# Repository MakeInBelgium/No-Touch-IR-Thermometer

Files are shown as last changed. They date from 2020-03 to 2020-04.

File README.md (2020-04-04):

# No-Touch-IR-Thermometer

## Introduction
Especially in the second phase and during the recovery of this pandemic, we will need to monitor both oursleves and our peers at work or in public places. One of the methods being used is checking whether someone has a fever or not. In order to do this without risking even more contamination, we can use *NO-TOUCH Thermometers*. Like the ones you use to test a baby's temperature.

We already anticipate a lack of enough available devices and are looking for **affordable** and **scalable** solutions. 

## GOALs
1) Using the occam's razor method we want to strip the concept of all unnecessary parts. The *need* we want to solve here is not knowing how high someone's temperature is. We merely want to know whether or not someone is a risk. Basic **triage**. Therefor we could eliminate an LED screen for example from the list of components and use just a GREEN/ORANGE/RED status indicator. 
2) We also want this to be something that van be (re)created wherever in the world with as little as possible equipment and components. This to drive down the cost, limit the skillset needed to finish the project, and limit the materials that need to be sourced.

## Concepts
There are 2 design concepts we have come up with. Both are based on the exact same principles but have a slightly different approach in building. Both are using an 8-bit Microcontroller that can be flashed through an Arduino set-up, and a [Melexis FIR](https://www.melexis.com/en/product/MLX90614/Digital-Plug-Play-Infrared-Thermometer-TO-Can) (Far Infra Red Temperature Sensor). Furthermore there's just a push button, a green/orange/red LED light and some electrical components. That's it!

### Project *Tiny-FIR*
The Tiny-FIR is based on the [ATtiny85](https://www.microchip.com/wwwproducts/en/ATtiny85) and will be a fully assembled PCB board. The designs for the board and all necessary information to recreate van be fond in the Tiny_FIR folder. 
*Audience*: this model is targeted at makerspaces and manufacturers

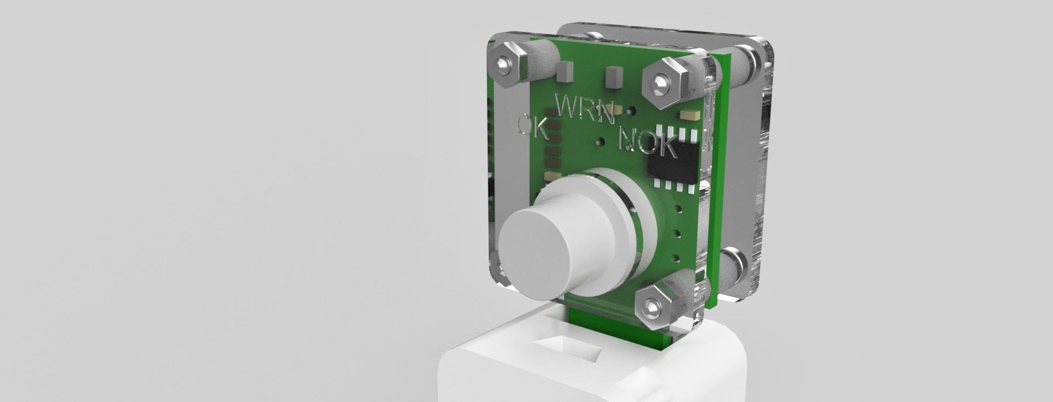
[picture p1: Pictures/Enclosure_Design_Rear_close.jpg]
Rear Close

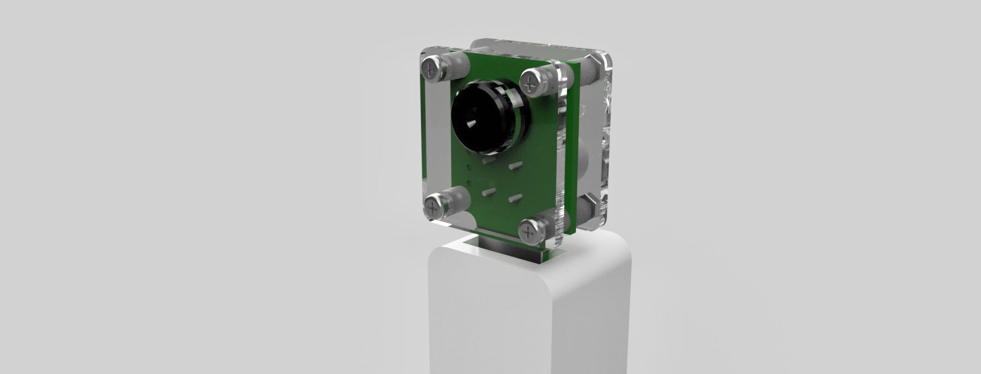
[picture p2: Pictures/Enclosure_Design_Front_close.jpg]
Rear Close


### Project *Mega-FIR*
the Mage-FIR is based on the [ATmega328](https://www.microchip.com/wwwproducts/en/ATmega328) and will be a default prototype breadboard with pin-though-hole components. The idea here is that all components are readily available off the shelf without the need for 3rd party manufacturers.
*Audience*: literally everyone with an Arduino board and a soldering iron.

doesn't she look cute?

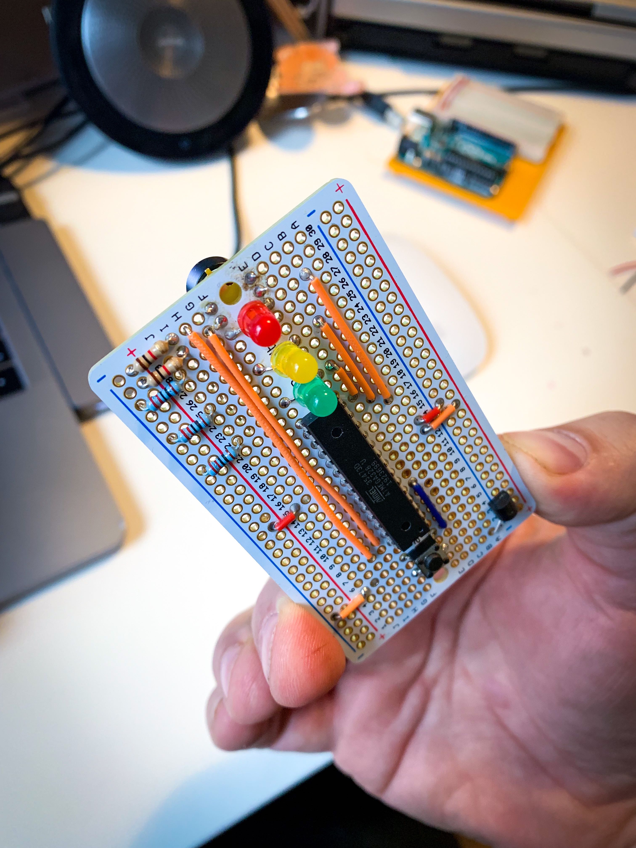
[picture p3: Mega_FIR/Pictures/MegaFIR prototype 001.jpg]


## Supported by:
* [EuroCircuits](https://www.eurocircuits.com/) - is helping with the first batches of the PCB-boards
* [MELEXIS](https://www.melexis.com/en) - has provided a first set sensors for the prototypes

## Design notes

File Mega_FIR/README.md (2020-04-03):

# The MegaFIR
 
## Introduction
The MegaFIR was the original concept of this no-touch-thermometer project. The ideas was for everyone with a soldering iron and a credit card to be able to build a fever triage thermometer. This is how it currently looks like in pretotyping. Feel free to check the [Electrical Diagram](https://github.com/MakeInBelgium/No-Touch-IR-Thermometer/blob/master/Mega_FIR/MegaFIR_ElectricalDiagram.md) document and the [Build of Materials (BoM)](https://github.com/MakeInBelgium/No-Touch-IR-Thermometer/blob/master/Mega_FIR/MegaFIR_BoM.md). 



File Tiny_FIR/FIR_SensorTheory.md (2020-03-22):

# Theory of operation
## Non-contact thermometers
**Disclaimer:** normal body temperature is considered to be 37°C; however, a wide variation is seen.<sup>[1](#cit1)</sup> So a measument taken  from a DIY device and judged to be either norminal or fibrile by that DIY device should *never be used in critical situations!*. The configuration of this concept is for TRIAGE puproses only.

There are several methods to measure body temperature. In the category of radiometric (infrared) measurements there are 3 main methods<sup>[2](#cit2)</sup>:
1. Tympanic thermometer (eardrum temperature)
2. Handheld skin thermometers (infrared sensors)
3. Thermal scanners (infrared cameras)

The Tiny_FIR project aims to build a sensor that uses this second measuring method, measuring the surface temperature of the skin. Because the sensor used in the Tiny_FIR and Mega_FIR project is also widely used for Tympanic thermometers, care must be taken to use and reference the right information online. The fibrile temperature is different for the eardrum than the skin surface and most probably a different compensation approuch should be used to determine the body temperature.

Most of the clinical radiometric thermometers that use the tympanic or skin surface measurements will report the body temperature. This temperature is a calculated, or indirect, measurement. Most of the Thermal cameras are general purpose devices that only report the direct measurent not the indirect body temperature.

The ideal fibrile threshold temperature of the skin surface seems to range between 37.5°C and 38°C. <sup>[3](#cit3)</sup>

## FIR sensors
The MLX90614 comes in many flavors. Melexis proposes to use the MLX90614-DCC. 
- D: This means the device is calibrated for 0.2degC accuracy around body temperature.
- C: The device is compensating for (but not eliminating) thermal gradients. 
- C: There is a 35 degree FOV.

In order to achieve as much accuracy as possible, there are some good practices to be followed:
### Ambient temperature
The temperature readout from the sensor (To) is compensated internally by the ambient temperature (Ta) as such: V<sub>ir</sub> = A x (To<sup>4</sup>-Ta<sup>4</sup>) The measurment of Ta is taken internally by a PTAT sensor. To achieve a higher accuracy this PTAT sensor measures the ambient temperature. In other words: the sensor should be in total thermal equilibrium with the surroundings.

The electronic design of the Tiny-FIR is in such a way so there is no large power-dissipation near the sensor. Furthermore, the sensor is kept powered all the time in between measurements as long as it is used (plugged into the USB powerbank). This avoid thermal gradients due to self-heating.

Lastly the user should be informed that usage of this sensor is limited to thermally static conditions. This means, for example, that **the sensor cannot be used in outdoor high-wind conditions** or when switching between area's with different ambient temperatures, like indoor and outdoor.

As a side-note it should be noted that a more complex compensation algorithm to calculated the body temperature should also use the ambiant temperature. The thermal gradient from body to skin surface will be depend on the ambiant temperature. So we can conclude that the fibrile temperature of the skin surface will also be ambient temperature dependent. This is also the reason why Ta is available for readout on the MLX90614.

### Field of view
The FOV of the sensor is defined as the region where it has more that 50% sensitivity. It is important that the surface that needs to be measured in entirely in the FOV. Some commercial thermometers achieve this by having two cocussed light beams converge, so when the dot allign the sensor is at the right distance.

Further investigation here is still required on how to implement this.

-----
# References:
1. : https://www.ncbi.nlm.nih.gov/books/NBK331/
2. : https://www.ncbi.nlm.nih.gov/books/NBK263242
3. : https://www.eurosurveillance.org/images/dynamic/EE/V14N06/art19115.pdf

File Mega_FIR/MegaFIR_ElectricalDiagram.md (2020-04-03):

# MegaFIR Electrical Diagram

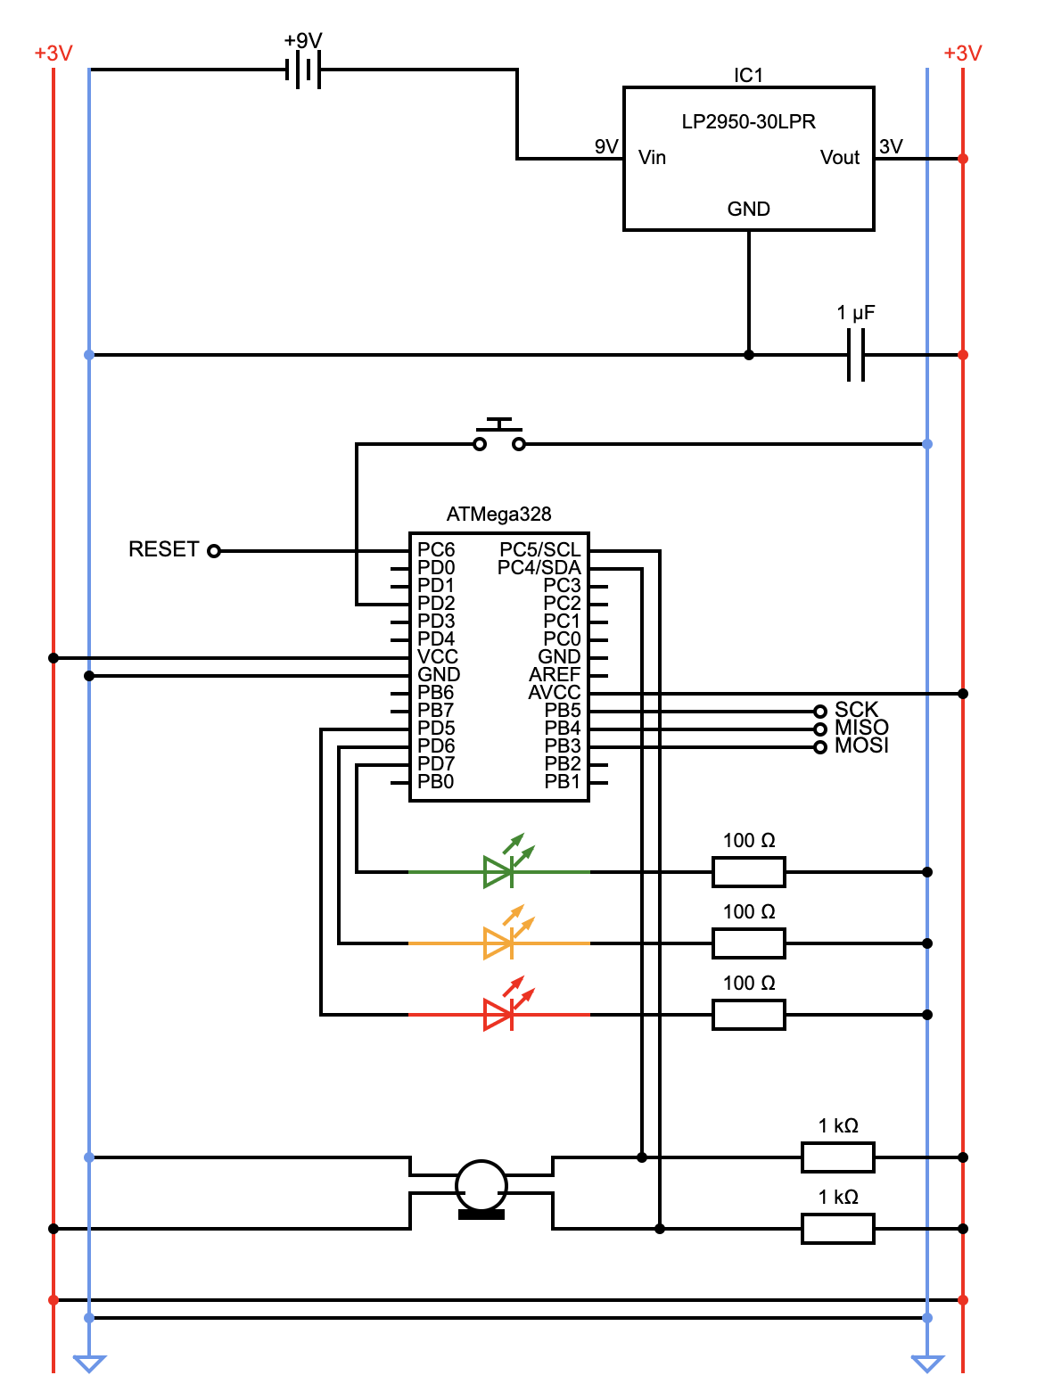
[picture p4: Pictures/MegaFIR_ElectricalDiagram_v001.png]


Note: the design is draw using Circuit Diagram, a free and Open-Source tool. [You can find the design here](https://www.circuit-diagram.org/circuits/e216c06a74a149ee9efb37499b95ee45).

## Description
This design is based on the idea of using a pin-through-hole proto-breadboard [(example)](https://www.adafruit.com/product/571) with 2x30 lanes and a +/- rail on each side. The lay-out is specifically designed to have the least amount of cables overlapping or even crossing the middle section. 

## PIN assignment
Some PINs on the ATmega are randomly chosen, some are very strict:
| ATmega PIN | Arduino PIN | Description | Strict? |
| --------: | --------: | -------- | :--------: | 
| 1 / PC6 | RESET | needed for programming the ATmega from the Arduino | X |
| 4 / PD2 | 2 | input from switch/button |  |
| VCC | VCC | Power | X |
| GND | GND | Ground | X |
| 11 / PD5 | 5 | Output LED red | |
| 12 / PD6 | 6 | Output LED green | | 
| 13 / PD7 | 7 | Output LED orange | | 
| 28 / PC5 | A5 | SCL (clock) port 1 on the MLX | X |
| 27 / PC4 | A4 | SDA (data) port 2 on the MLX | X |
| 20 / AVCC | AVCC | Power | X |
| 19 / PB5 | 13 | SCK - needed for programming the ATmega from the Arduino | X |
| 18 / PB4 | 12 | MISO - needed for programming the ATmega from the Arduino | X |
| 17 / PB3 | 11 | MOSI - needed for programming the ATmega from the Arduino | X |

## Arduino & ATmega pin alignment

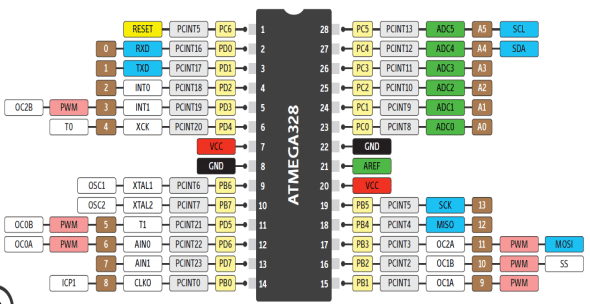
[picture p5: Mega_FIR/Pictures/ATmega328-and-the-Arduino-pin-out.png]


*sorry I can't find and quote the original source of this image. it was the best Google search result

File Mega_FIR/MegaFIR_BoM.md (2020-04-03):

# MegaFIR Build of Materials:

| # | Description | Manufacturer-ID | Farnel Code | Other Links | €/piece |
|----------|----------|----------|----------|---------|---------:|
| 1 | Melexis Sensor MLX90614 | MLX90614ESF-DCC-000 | / | [Mouser link](https://eu.mouser.com/ProductDetail/Melexis/MLX90614ESF-DCC-000-TU?qs=%2Fha2pyFaduia27wdAojmz0Gw0WK2y0hzp6DRConqg3jzJRxxBtPVbyFno%252B8k7uZuTdJKb%252Bns4tW7oym5d884Wg%3D%3D) | / |
| 1 | ATmega328 Microprocessor | ATMEGA328-PU | 1972087 [link(.be)](https://be.farnell.com/microchip/atmega328-pu/mcu-8bit-atmega-20mhz-dip-28/dp/1972087) | | €1.7000 |
| 1 | LDO Voltage Regulator (3V) | LP2950-30LPR | 3122121 [link(.be)](https://be.farnell.com/texas-instruments/lp2950-30lpr/ic-ldo-volt-reg-3v-0-1a-to-92/dp/3122121) | | €0,368 |
| 1 | 1µF electrolytic capacitor |	MCF 0.25W 100R | 9339043 [link(.be)](https://be.farnell.com/rubycon/50ml1mefc4x5/cap-1-f-50v-20/dp/8126933) | | €0.0245 |
| 1 | Tactile Switch | B3F1060 | 1960944 [link(.be)](https://be.farnell.com/omron/b3f1060/switch-flat-6x6x7-100gf/dp/1960944) | | €0.2580 |
| 1 | LED - Green T-1 3/4 (5mm), 20 mA, 2 V | L-57GGD | 2217954 [link(.be](https://be.farnell.com/kingbright/l-57ggd/led-bi-polar-5mm-green/dp/2217954) | | €0.3180 |
| 1 | LED - Yellow T-1 3/4 (5mm), 20 mA, 2 V |	L-57YYD | 2217955 [link(.be)](https://be.farnell.com/kingbright/l-57yyd/led-bi-polar-5mm-yellow/dp/2217955) | | €0.1530 |
| 1 | LED - Red T-1 3/4 (5mm), 20 mA, 2 V | L-57IID | 2217953 [link(.be)](https://be.farnell.com/kingbright/l-57iid/led-bi-polar-5mm-red/dp/2217953) | | €0.3130
| 2 | Resistor 1kΩ | MCF 0.25W 1K | 9339051 [link(.be)](https://be.farnell.com/multicomp/mcf-0-25w-1k/res-1k-5-250mw-axial-carbon-film/dp/9339051) | | €0.0245  |
| 3 | Resistor 100Ω | 	MCF 0.25W 100R | 9339043 [link(.be)](https://be.farnell.com/multicomp/mcf-0-25w-100r/res-100r-5-250mw-axial-carbon/dp/9339043)  | | €0,0245 |
| 1 | 9V Battery Snap Connector | Keystone 2238 | 1650675 [link(.be)](https://be.farnell.com/keystone/2238/battery-strap-pp3/dp/1650675) | | €1.6900 |

## Cost
The total build of materials for a MegaFIR will set you back €6 for the components. Additional costs are:
* The Melexis sensor
* a 9V battery
* a breadboard
* some wiring
* a case* 

*:we'll come up with some ideas later, maybe even a 3D printing file

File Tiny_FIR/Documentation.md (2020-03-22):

# Theory of operation
## Non-contact thermometers
First a small disclaimer. Normal body temperature is considered to be 37°C; however, a wide variation is seen.<sup>[1](#cit1)</sup> So a measument taken  from a DIY device ánd judged to be either norminal or fibrile by that DIY device should *never be used in critical situations!*

There are several methods to measure this body temperature. In the category of radiometric (infrared) measurements there are 3 main methods<sup>[2](#cit2)</sup>:
1. Tympanic thermometer (eardrum temperature)
2. Handheld infrared skin thermometers
3. Thermal scanners (infrared cameras)

The Tiny_FIR project aims to build a sensor that uses this second measuring method, measuring the surface temperature of the skin. Because the sensor used in the Tiny_FIR project is also widely used for Tympanic thermometers, care must be taken to use and reference the right information online. The fibrile temperature is different for the eardrum than the skin surface and most probably a different compensation approuch should be used to determine the body temperature.

Most of the clinical radiometric thermometers that use the tympanic or skin surface measurements will report the body temperature. This temperature is a calculated, or indirect, measurement. Most of the Thermal cameras are general purpose devices that only report the direct measurent not the indirect body temperature.

The ideal fibrile threshold temperature of the skin surface seems to range between 37.5°C and 38°C. <sup>[3](#cit3)</sup>

## FIR sensors
The MLX90614 comes in many flavors. Melexis proposes to use the MLX90614-DCC. 
- D: This means the device is calibrated for 0.2degC accuracy around body temperature.
- C: The device is compensating for (but not eliminating) thermal gradients. 
- C: There is a 35 degree FOV.

In order to achieve as much accuracy as possible, there are many good practices to be followe:
### Ambient temperature
The temperature readout from the sensor (To) is compensated internally by the ambient temperature (Ta) as such: V<sub>ir</sub> = A x (To<sup>4</sup>-Ta<sup>4</sup>) The measurment of Ta is taken internally by a PTAT sensor. So to achieve high accuracy this PTAT sensor should measure the actual ambiant temperature. In other words: the sensor should be in total thermal equilibrium with the surroundings.

The electronic design of the Tiny-FIR is in such a way so there is no large power-dissipation near the sensor. Furthermore, the sensor is kept powered all the time in between measurements as long as it is used (plugged into the USB powerbank). This avoid thermal gradients due to self-heating.

Lastly the user should be informed that usage of this sensor is limited to thermally static conditions. This means, for example, that the sensor cannot be used in outdoor high-wind conditions or when switching between area's with different ambient temperatures, like indoor and outdoor.

As a side-note it should be noted that a more complex compensation algorithm to calculated the body temperature should also use the ambiant temperature. The thermal gradient from body to skin surface will be depend on the ambiant temperature. So we can conclude that the fibrile temperature of the skin surface will also be ambient temperature dependent. This is also the reason why Ta is available for readout on the MLX90614.

### Field of view
The FOV of the sensor is defined as the region where it has more that 50% sensitivity. It is important that the surface that needs to be measured in entirely in the FOV. Some commercial thermometers achieve this by having two cocussed light beams converge, so when the dot allign the sensor is at the right distance.

Further investigation here is still required on how to implement this.

# References:
1. : https://www.ncbi.nlm.nih.gov/books/NBK331/
2. : https://www.ncbi.nlm.nih.gov/books/NBK263242
3. : https://www.eurosurveillance.org/images/dynamic/EE/V14N06/art19115.pdf

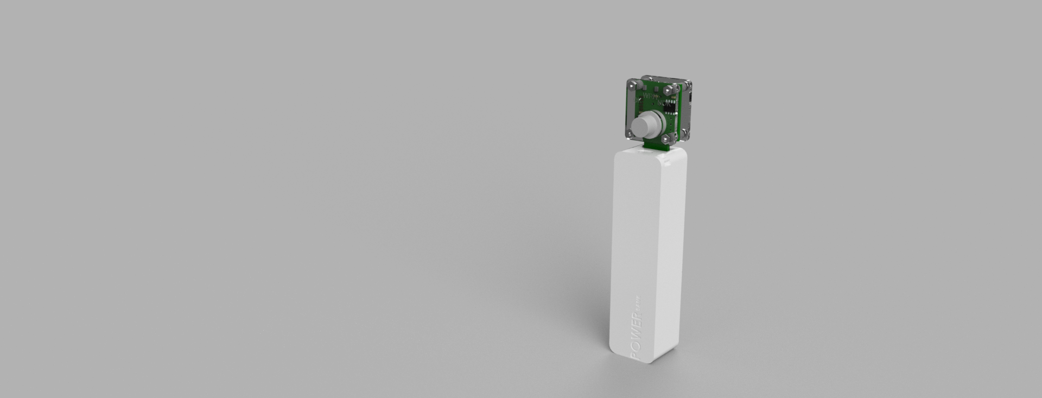
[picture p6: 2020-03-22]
Pictures/Enclosure_Design_Back_far.png

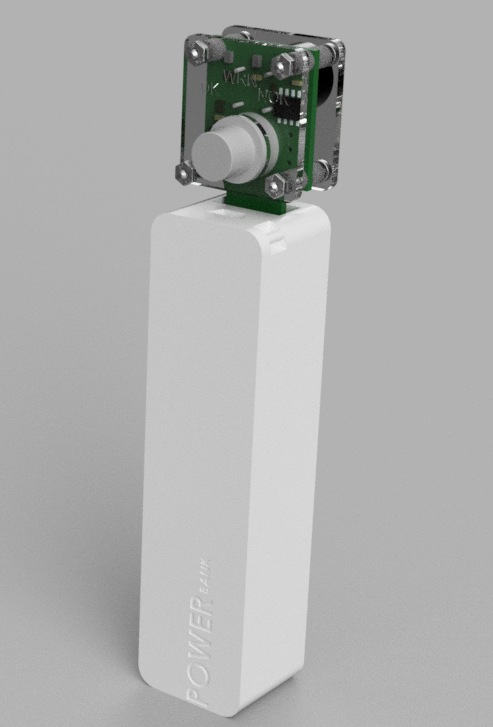
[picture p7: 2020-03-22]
Pictures/TinyFIR_3Drender01.png

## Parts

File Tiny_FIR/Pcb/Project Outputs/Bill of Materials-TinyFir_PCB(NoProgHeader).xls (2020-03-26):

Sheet: PCB
Designator | Quantity | Comment | Description | Footprint | Farnell code
C1, C3 | 2 | 100n | CAPACITOR Ceramic Multi-Layer X7R; 100nF; 50V; 0603; Tolerance, +/-10%; Temp, op. -55°C to +125°C | CAPC1608[0603]N | 2581045
LED1 | 1 | KP-2012SRC | LED SMD 0805 super bright red clear | DIO2012[0805] | 3015159
LED2 | 1 | KP-2012SYC | LED SMD 0805 super bright yellow clear | DIO2012[0805] | 2099243
LED3 | 1 | KP-2012MGC | LED SMD 0805 mega green clear | DIO2012[0805] | 2099239
R1, R2 | 2 | 1K | Resistor Thick Film; 1K; 0603; 0.1W; 1%; 50V; 100ppm/DegC | RESC1608[0603]N | 2694685
R3, R4, R5 | 3 | 180R | Resistor Thick Film; 180R; 0603; 0.1W; 1%; 50V; 100ppm/DegC | RESC1608[0603]N | 2694050
SW1 | 1 | D6R | SPST Momentary Key Switches | SW_SPST_PB_CK | 1201375
U1 | 1 | MLX90614 | MLX90614 Infra Red Thermometer in TO-39 | MLX90614_**C
U2 | 1 | Attiny xx2 | AVR® Microcontroller with Core Independent Peripherals and picoPower® Technology | SOIC127P600-8_straight | 2915533
U3 | 1 | MIC5501-3.0YM5 | Voltage Regulator, FIxed LDO, Vo=+3V, Io=300mA, SOT23-5 | SOT23-5 | 2857640

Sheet: Enclosure
Quantity | Item | Description | RS-nummer
8 | Spacer | 4mm High Polyamide Round Spacer With 4mm Diameter and 2.2mm Bore Diameter | 184-2579
4 | Screw | RS PRO Pozidriv Pan Head A2 304 Stainless Steel Machine Screw, M2, 16mm | 179-5689
4 | Nut | RS PRO Stainless Steel, Hex Nut, M2 | 248-4551

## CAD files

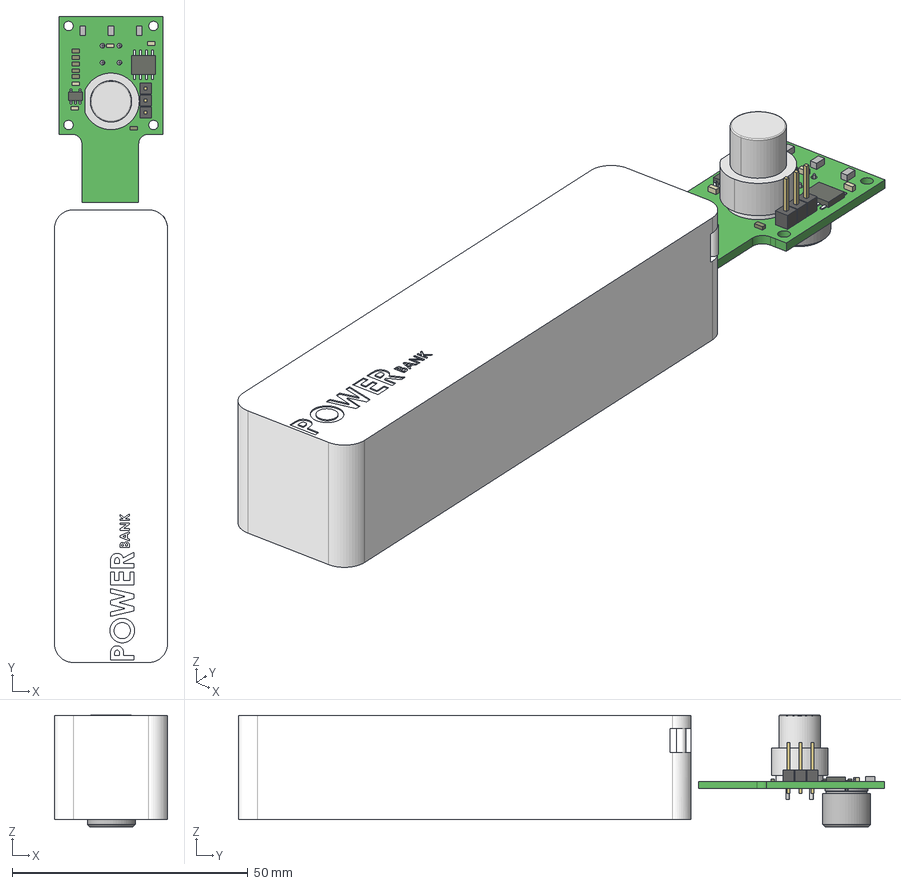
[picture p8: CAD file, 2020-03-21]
Tiny_FIR/Pcb/Project Outputs/TinyFIR.step
24.0 x 137.0 x 23.7 mm
MLX90614_DCC
Extruded x 45
User_Library-C_K_D6R10_gris
PowerBank

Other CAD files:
Tiny_FIR/Pcb/Project Outputs/TinyFIR.DXF

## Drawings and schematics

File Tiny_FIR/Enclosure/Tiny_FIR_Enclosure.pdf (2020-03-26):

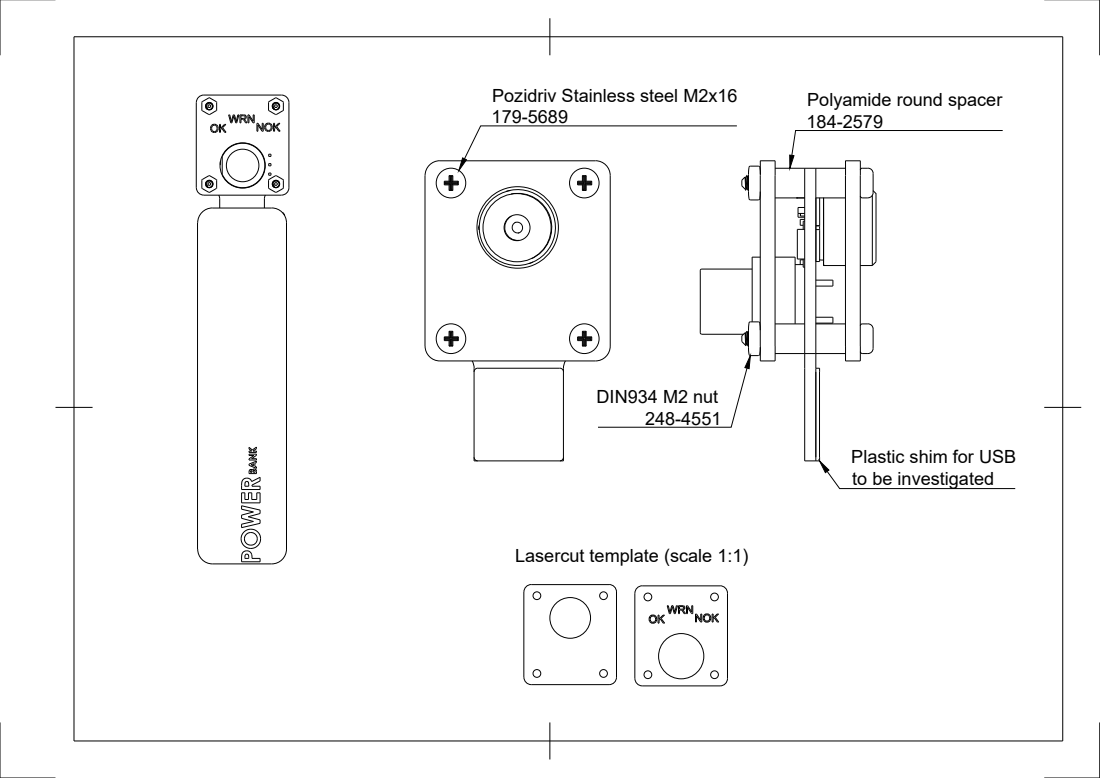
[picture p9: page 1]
DIN934 M2 nut

Pozidriv Stainless steel M2x16

Polyamide round spacer

Plastic shim for USB
to be investigated

Lasercut template (scale 1:1)

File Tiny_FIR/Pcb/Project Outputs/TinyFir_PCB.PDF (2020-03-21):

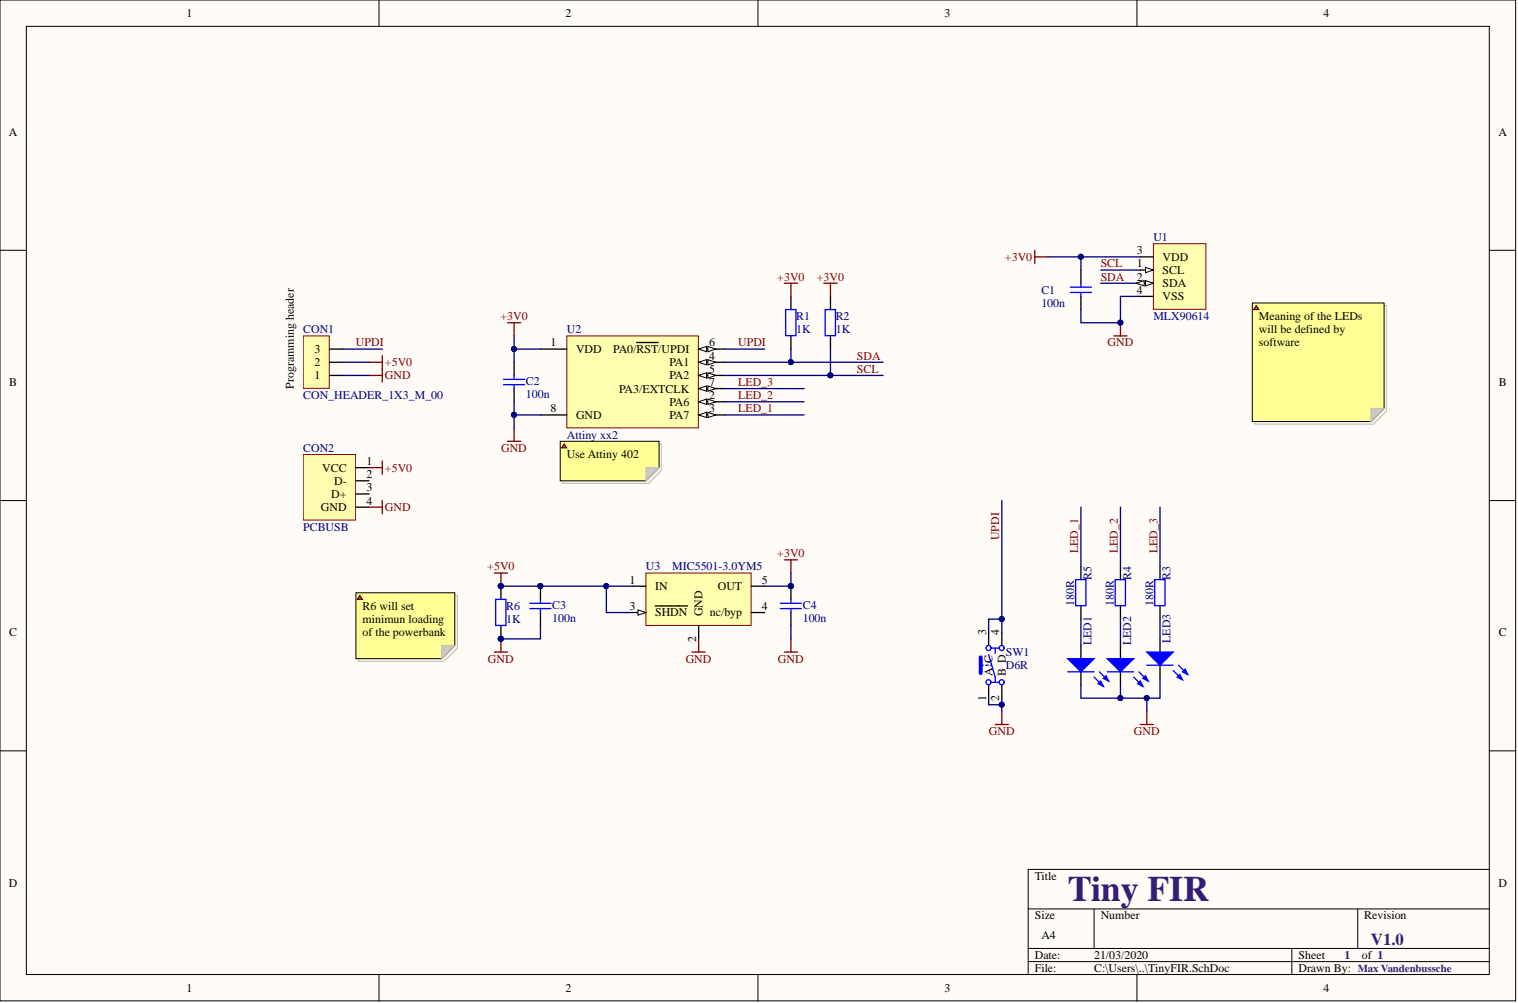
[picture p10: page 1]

will be defined by
software

Designator | Quantity | Comment | Description | Footprint
C1, C3 | | 2 100n | CAPACITOR Ceramic Multi-Layer X7R; 100nF; 50V; 0603; Tolerance, +/-10%; Temp, op. | -CAPC1608[0603]N
LED1 | | 1 KP-2012SRC | LED SMD 0805 super bright red clear | DIO2012[0805]
LED2 | | 1 KP-2012SYC | LED SMD 0805 super bright yellow clear | DIO2012[0805]
LED3 | | 1 KP-2012MGC | LED SMD 0805 mega green clear | DIO2012[0805]
R1, R2 | | 2 1K | Resistor Thick Film; 1K; 0603; 0.1W; 1%; 50V; 100ppm/DegC | RESC1608[0603]N
R3, R4, R5 | | 3 180R | Resistor Thick Film; 180R; 0603; 0.1W; 1%; 50V; 100ppm/DegC | RESC1608[0603]N
SW1 | | 1 D6R | SPST Momentary Key Switches | SW_SPST_PB_CK
U1 | | 1 MLX90614 | MLX90614 Infra Red Thermometer in TO-39 | MLX90614_**C
U2 | | 1 Attiny xx2 | A VR® Microcontroller with Core Independent Peripherals | SOIC127P600-8_straight
U3 | | 1 MIC5501-3.0YM5 | and picoPower® Technology Voltage Regulator, FIxed LDO, Vo=+3V, Io=300mA, SOT23-5 | SOT23-5

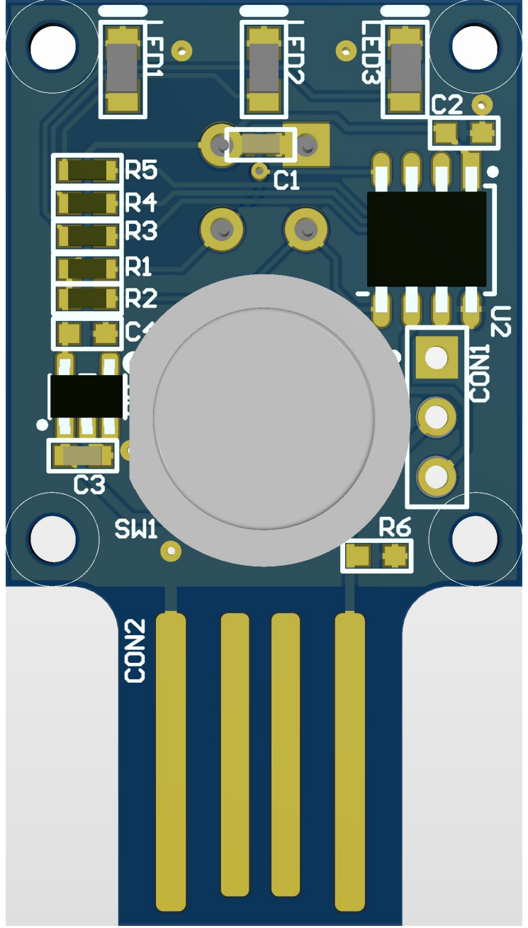
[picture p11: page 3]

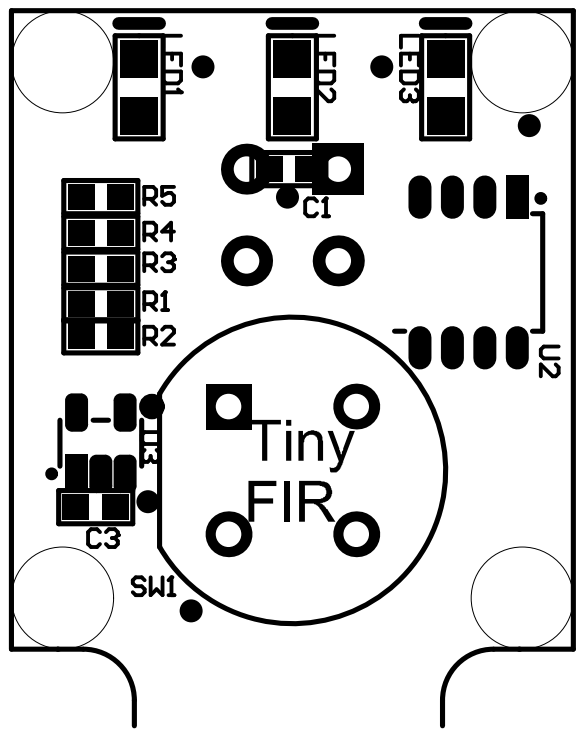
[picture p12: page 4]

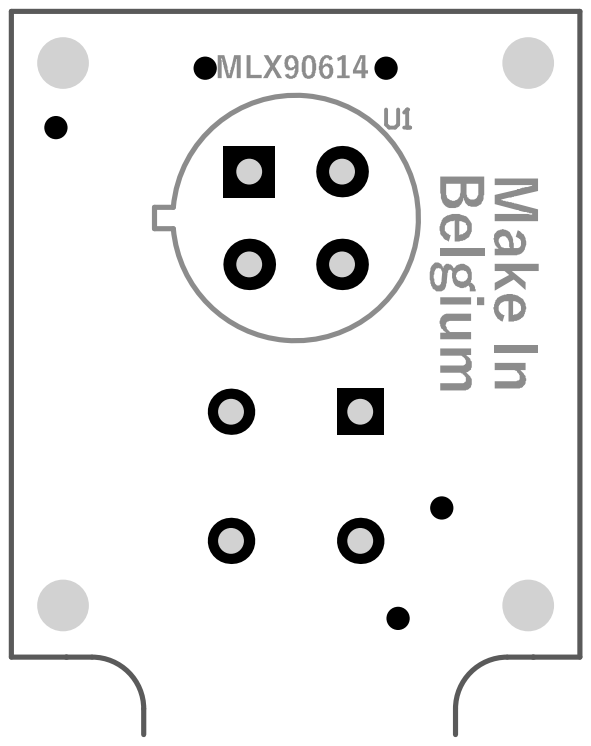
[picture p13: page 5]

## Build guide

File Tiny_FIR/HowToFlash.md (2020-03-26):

So, you have a Tiny_FIR contraption in your hand? And you want the MCU to start making measurements?
Here is how you get the code running on the onboard ATtiny402:
1. <u>Get the JTAG2UPDI project:</u>
Download or clone the [JTAG2UPDI](https://github.com/ElTangas/jtag2updi) repository from ElTangas.
(Maybe it would be nice to have this repo as a submodule?)
2. <u>Compile JTAG2UPDI code and flash a tool:</u>:
Follow the instruction in the jtag2updi repo. You can even just use the arduino environment to compile an flash an Arduino Uno! Isn't that simple?
3. <u>(optional) Check communication with the ATtiny ROM bootloader using avrdude:</u>
You can execute the following avrdude command to read the device signature. Replace the comport number with the correct comport for the Arduino on your PC.
```
.\avrdude.exe -C .\avrdude.conf -c jtag2updi -P com17 -p t402
avrdude.exe: AVR device initialized and ready to accept instructions

Reading | ################################################## | 100% 0.30s

avrdude.exe: Device signature = 0x1e9227 (probably t402)

avrdude.exe done.  Thank you.
```
4.<u>Flashing the firmware to the ATTiny:</u>
WIP....

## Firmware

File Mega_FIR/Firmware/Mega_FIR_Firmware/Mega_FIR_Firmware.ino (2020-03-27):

#include "Adafruit_MLX90614.h"

#define MLX90614_ERROR_BIT 0x8000

#define PIN_LOW_FOR_SERIAL_MONITORING A0 // If this pin attached to GND, monitoring messages will be sent on the serial port
#define PIN_LED_OK                    A1 // Green LED
#define PIN_LED_WARN                  A2 // Yellow LED
#define PIN_LED_NOK                   A3 // Red LED
#define PIN_LOW_FOR_TRIGGER           A4 // When pulled low, a new measurement cycle is triggered (can be used to connect a push-button)

#define STATUS_OK             0
#define STATUS_WARN           1
#define STATUS_NOK            2
#define STATUS_ERROR          3
#define STATUS_INITIALIZING   4

/*
 * Temperature tresholds:
 *
 *    Temperature in °C = ( raw sensor value * 0.02 ) - 273.15
 * => Raw sensor value = ( Temperature in °C + 273.15 ) * 50
 *
 */

// TODO: values need to be verified by med, still dummy values
const uint16_t TEMP_TH_TOO_LOW =  ( ( 34.5 + 273.15 ) * 50 ) + 0.5;
const uint16_t TEMP_TH_OK =       ( ( 36.5 + 273.15 ) * 50 ) + 0.5;
const uint16_t TEMP_TH_WARN =     ( ( 38.0 + 273.15 ) * 50 ) + 0.5;

// Globals
Adafruit_MLX90614 mlx = Adafruit_MLX90614();
bool serialMonitoring;    // If true, monitoring messages are sent over the serial port
uint32_t millisStart;


void setup(){

  // Init all the things
  pinSetup();
  mlx.begin();
  
  // No messages are sent on the serial port
  // unless PIN_LOW_FOR_SERIAL_MONITORING is connected to GND
  serialMonitoring = false;
  if( !digitalRead( PIN_LOW_FOR_SERIAL_MONITORING ) ){
    serialMonitoring = true;
    Serial.begin( 9600 );
  }
}

void loop(){

  // Wait until button is pushed
  setLedsAllOff();
  if( !buttonPushed() ){
    return;
  }

  millisStart = millis();

  // Initialize statuses array
  uint16_t statuses [200]; // Keep last x statuses
  uint16_t numStatuses = sizeof( statuses ) / sizeof( uint16_t ); // The number of elements in the array
  for( uint16_t i = 0; i < numStatuses; i++ ){
    statuses[i] = STATUS_INITIALIZING;
  }

  uint8_t worst = STATUS_OK;
  for( uint16_t i = 0; i < numStatuses; i++ ){
    if( !buttonPushed() ) return;
    uint16_t obj1TempRaw = readTempObj1Raw();
    if( serialMonitoring ) serialPrintMeasurement( obj1TempRaw );

    uint8_t status = getStatus( obj1TempRaw );
    statuses[i] = status;
    worst = max( worst, status );
    displayStatus( STATUS_INITIALIZING );
    delay( 5 );
  }
  
  // Display the status
  while( buttonPushed() ){
    displayStatus( worst );
  }

  delay( 50 ); // Debounce
}

void pinSetup(){
  pinMode( PIN_LOW_FOR_SERIAL_MONITORING, INPUT_PULLUP);
  pinMode( PIN_LOW_FOR_TRIGGER, INPUT_PULLUP);
  pinMode( PIN_LED_OK, OUTPUT );
  pinMode( PIN_LED_WARN, OUTPUT );
  pinMode( PIN_LED_NOK, OUTPUT );
}

bool buttonPushed(){
  return !digitalRead( PIN_LOW_FOR_TRIGGER );
}

uint16_t readTempObj1Raw(){
  return mlx.read16(MLX90614_TOBJ1);
}

uint8_t getStatus( uint16_t rawValue ){
  // MSB = 1?  => Sensor read error (Datasheet p. 30)
  if( ( rawValue & MLX90614_ERROR_BIT ) == MLX90614_ERROR_BIT){
    if( serialMonitoring ) Serial.println( " - Sensor error => STATUS_ERROR" );
    return STATUS_ERROR;
  }
  
  if( rawValue <= TEMP_TH_TOO_LOW ){
    if( serialMonitoring ) Serial.println( " - T too low => STATUS_ERROR" );
    return STATUS_ERROR;
  }
  
  if( rawValue <= TEMP_TH_OK ){
    if( serialMonitoring ) Serial.println( " - T ok => STATUS_OK" );
    return STATUS_OK;
  }
  
  if( rawValue <= TEMP_TH_WARN ){
    if( serialMonitoring ) Serial.println( " - T above ok => STATUS_WARN" );
    return STATUS_WARN;
  }
  if( serialMonitoring ) Serial.println( " - T above warning => STATUS_NOK" );
  return STATUS_NOK;
}

void setLedsAllOff(){
  digitalWrite( PIN_LED_OK, LOW );
  digitalWrite( PIN_LED_WARN, LOW );
  digitalWrite( PIN_LED_NOK, LOW );
}

void displayStatus( uint8_t status ){
  switch(status){
    case STATUS_OK:{
      digitalWrite( PIN_LED_OK, HIGH );
      digitalWrite( PIN_LED_WARN, LOW );
      digitalWrite( PIN_LED_NOK, LOW );
      break;
    }

    case STATUS_WARN:{
      digitalWrite( PIN_LED_OK, LOW );
      digitalWrite( PIN_LED_WARN, HIGH );
      digitalWrite( PIN_LED_NOK, LOW );
      break;
    }

    case STATUS_NOK:{
      digitalWrite( PIN_LED_OK, LOW );
      digitalWrite( PIN_LED_WARN, LOW );
      digitalWrite( PIN_LED_NOK, HIGH );
      break;
    }
    
    case STATUS_ERROR:{
      // Make the warning LED flash
      uint32_t m = millis() % 200;
      bool ledIsOn = m < 20;
      digitalWrite( PIN_LED_OK, LOW );
      digitalWrite( PIN_LED_WARN, ledIsOn );
      digitalWrite( PIN_LED_NOK, LOW );
      break;
    }

    case STATUS_INITIALIZING:{
      // Make the warning LED flash
      uint32_t m = ( millis() - millisStart ) % 450;
      digitalWrite( PIN_LED_OK, m < 150 );
      digitalWrite( PIN_LED_WARN, m >= 150 && m < 300 );
      digitalWrite( PIN_LED_NOK, m >= 300 );
      break;
    }
  }
}

void serialPrintMeasurement( uint16_t tempRaw ){
  Serial.print( millis() );
  Serial.print( " - Sensor value: " );
  Serial.print( tempRaw ); 
  Serial.print( " = ");
  Serial.print( rawTempToCelcius( tempRaw ) );
  Serial.print( "°C " );
}

double rawTempToCelcius( uint16_t raw ){
  return raw * 0.02 - 273.15;
}

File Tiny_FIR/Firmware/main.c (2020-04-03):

#include <atmel_start.h>
#include <avr/io.h>
#include <util/delay.h>
#include <i2c_simple_master.h>

// MLX90614 Datasheet: https://www.melexis.com/-/media/files/documents/datasheets/mlx90614-datasheet-melexis.pdf
#define MLX90614_I2CADDR 0x5A
#define MLX90614_REG_RAWIR1 0x04
#define MLX90614_REG_RAWIR2 0x05
#define MLX90614_REG_TA 0x06
#define MLX90614_REG_TOBJ1 0x07
#define MLX90614_REG_TOBJ2 0x08

#define MLX90614_ERROR_BIT 0x8000

#define LED_OK_bm	PIN3_bm
#define LED_WARN_bm	PIN6_bm
#define LED_NOK_bm	PIN7_bm

#define STATUS_OK			0
#define STATUS_WARN			1
#define STATUS_NOK			2
#define STATUS_ERROR		3
#define STATUS_INITIALIZING	4

/*
* Temperature tresholds:
*
*    Temperature in °C = ( raw sensor value * 0.02 ) - 273.15
* => Raw sensor value = ( Temperature in °C + 273.15 ) * 50
*
*/

// TODO: values need to be verified by med, still dummy values
const uint16_t TEMP_TH_TOO_LOW =  ( ( 34.5 + 273.15 ) * 50 ) + 0.5;
const uint16_t TEMP_TH_OK =       ( ( 36.5 + 273.15 ) * 50 ) + 0.5;
const uint16_t TEMP_TH_WARN =     ( ( 38.0 + 273.15 ) * 50 ) + 0.5;

// Globals
uint32_t millis; // Approximates the run time in milliseconds (no need for 100% accuracy, just used to blink the leds)

// Function declarations
void pinSetup();
void setLedsAllOff();
void setLEDstatus(uint8_t status);
uint16_t readTempObj1Raw(void);
uint8_t getStatus( uint16_t rawValue );
void displayStatus( uint8_t status );

int main(void){
	
	// When we arrive here it means we just had a reset-event. Most-probably because the user pushed the button!
	millis = 0;
	uint16_t loopTime = 80; // Measure-loop takes about 80ms

	// Init our little MCU: pins, drivers, ...
	pinSetup();
	
	// Give the sensor a small time to start up
	// (MCU seems to start up faster than sensor => if the MCU communicates too soon with the sensor, 0-values are 'measured')
	setLedsAllOff();
	PORTA.OUTSET = LED_OK_bm;
	_delay_ms( 100 );
	millis += 2 * loopTime; // Gives a smoother blink-effect on startup
	
	atmel_start_init();

	// Initialize statuses array
	uint16_t statuses [25]; // Keep last x statuses
	uint16_t numStatuses = sizeof( statuses ) / sizeof( uint16_t ); // The number of elements in the array
	for( uint16_t i = 0; i < numStatuses; i++ ){
		statuses[i] = STATUS_INITIALIZING;
	}
	
	// Start the measure loop
	uint8_t worst = STATUS_OK;
	for( uint16_t i = 0; i < numStatuses; i++ ){

		uint16_t obj1TempRaw = readTempObj1Raw();

		uint8_t status = getStatus( obj1TempRaw );
		statuses[i] = status;
		worst = status > worst ? status : worst;
		displayStatus( STATUS_INITIALIZING );

		millis += loopTime;
	}

	while(true)
	{
		displayStatus( worst );
		_delay_ms( loopTime );
		millis += loopTime;
	}
}

void pinSetup(){
	PORTA.DIRSET = LED_OK_bm | LED_WARN_bm | LED_NOK_bm ;
}

uint16_t readTempObj1Raw(){
	uint16_t regValue = I2C_0_read2ByteRegister(MLX90614_I2CADDR, MLX90614_REG_TOBJ1);
	return regValue << 8 | regValue >> 8;
}

uint8_t getStatus( uint16_t rawValue ){
	// MSB = 1?  => Sensor read error (Datasheet p. 30)
	if( ( rawValue & MLX90614_ERROR_BIT ) == MLX90614_ERROR_BIT){
		return STATUS_ERROR;
	}
	
	if( rawValue <= TEMP_TH_TOO_LOW ){
		return STATUS_ERROR;
	}
	
	if( rawValue <= TEMP_TH_OK ){
		return STATUS_OK;
	}
	
	if( rawValue <= TEMP_TH_WARN ){
		return STATUS_WARN;
	}
	return STATUS_NOK;
}

void setLedsAllOff(){
	PORTA.OUTCLR = LED_OK_bm | LED_WARN_bm | LED_NOK_bm;
}

void displayStatus( uint8_t status ){
	
	switch(status){
		case STATUS_OK:{
			PORTA.OUTCLR = LED_WARN_bm | LED_NOK_bm;
			PORTA.OUTSET = LED_OK_bm;
			break;
		}

		case STATUS_WARN:{
			PORTA.OUTCLR = LED_OK_bm | LED_NOK_bm;
			PORTA.OUTSET = LED_WARN_bm;
			break;
		}

		case STATUS_NOK:{
			PORTA.OUTCLR = LED_OK_bm | LED_WARN_bm;
			PORTA.OUTSET = LED_NOK_bm;
			break;
		}
		
		case STATUS_ERROR:{
			// Make the warning LED flash
			uint32_t m = millis % 240;
			if( m < 20 ){
				PORTA.OUTCLR = LED_OK_bm | LED_NOK_bm;
				PORTA.OUTSET = LED_WARN_bm;
				
			}
			else{
				PORTA.OUTCLR = LED_OK_bm | LED_WARN_bm | LED_NOK_bm;
			}
			break;
		}

		case STATUS_INITIALIZING:{
			// Make the warning LED flash
			uint32_t m = millis % 460;
			PORTA.OUTCLR =  (( m < 160 ) ? 0 : LED_OK_bm )
			| (( m >= 160 && m < 320 ) ? 0 : LED_WARN_bm )
			| (( m >= 320 ) ? 0 : LED_NOK_bm );
			PORTA.OUTSET = (( m < 160 ) ? LED_OK_bm : 0 )
			| (( m >= 160 && m < 320 ) ? LED_WARN_bm : 0 )
			| (( m >= 320 ) ? LED_NOK_bm : 0 );
			break;
		}
	}
}

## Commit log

2020-03-20 Initial commit of the whole Altium Designer project. Create .gitignore for Altiums overzealous logging.
    [TinyFIR.GBL, TinyFIR.GBO, TinyFIR.GBS, TinyFIR.GM1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]
2020-03-20 Create TinyFIR.step
    Add 3D step file export, usefull for enlcosure creation.
    [TinyFIR.step]
2020-03-20 New version of PCB
    Changes:
    - New big push button
    - A bit wider
    - Clearance for mounting houles
    [TinyFIR.GBL, TinyFIR.GBO, TinyFIR.GBS, TinyFIR.GM1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]
2020-03-20 Update main.c
    Clarify LED-pin functionality
2020-03-21 First rough prototype version (1 measurement on 1 sensor)
2020-03-21 Update to the PCB with correct sensor footprint
    [TinyFIR.DXF, TinyFIR.GBL, TinyFIR.GBO, TinyFIR.GBS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]
2020-03-24 Adapted & tested with real sensor
2020-03-26 PCB update 2
    Finalizing PCB outputs + Pick and Place file.
    [Bill of Materials-TinyFir_PCB(NoProgHeader).xls, TinyFIR.GBO, TinyFIR.GTL]
2020-03-26 PCB ouput update for eC
    Changed from Gerber X1 to X2
    Changed CPL file to CSV.
    [Pick Place for TinyFIR(NoProgHeader).csv, TinyFIR.GBL, TinyFIR.GBO, TinyFIR.GBS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]
2020-03-26 Update to BOM
    Now including the enclosure nuts and bolts.
    [Bill of Materials-TinyFir_PCB(NoProgHeader).xls]
2020-03-28 First working version ATtiny 402 + sensor via I²C
2020-03-28 Fixed outlining + smoother behavior of green led at startup
2020-04-01 Create MegaFIR Build of Materials
